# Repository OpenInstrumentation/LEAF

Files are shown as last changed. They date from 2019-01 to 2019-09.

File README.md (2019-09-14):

# LEAF
Logger for Environmental and Atmospheric Factors

CC-BY-SA 2019, A. Matheny, P. Marchetto, J. Powell, A. Rechner, J-y. Chuah, and S. Pierce

BoM: https://docs.google.com/spreadsheets/d/e/2PACX-1vQ8v-ukr38iTDn-cAedqp6OXnIay0lwoVsFbz_EMlWamA66PgREalaegVoSEzRlPvawVt73zznOhLpU/pubhtml or any of the BoM files above.

# Purpose
The LEAF is designed to be a modular sensing system, capable of measuring meteorological, hydrological, and other environmental parameters. In the design detailed in this repository, it was used to measure canopy throughfall of rain, soil moisture, and microclimate meteorological parameters, along with branch movement in the same tree the throughfall measurements were being made in.

# Files
The files in this repository are what's needed to program the different nodes of the sensing system network. The ground .ino file is different from the branches because it measures soil moisture as well; both of the .ino files are designed to be uploaded via Particle's online IDE at http://build.particle.io/. The catalog file includes all of the different items as priced at the time of the build, and the BoM includes direct links to them. The deployment file shows roughly what the initial instance looked like in its first deployment. The .brd and .sch files are Eagle board and schematic files, respectively, used to make PCBs for the system.

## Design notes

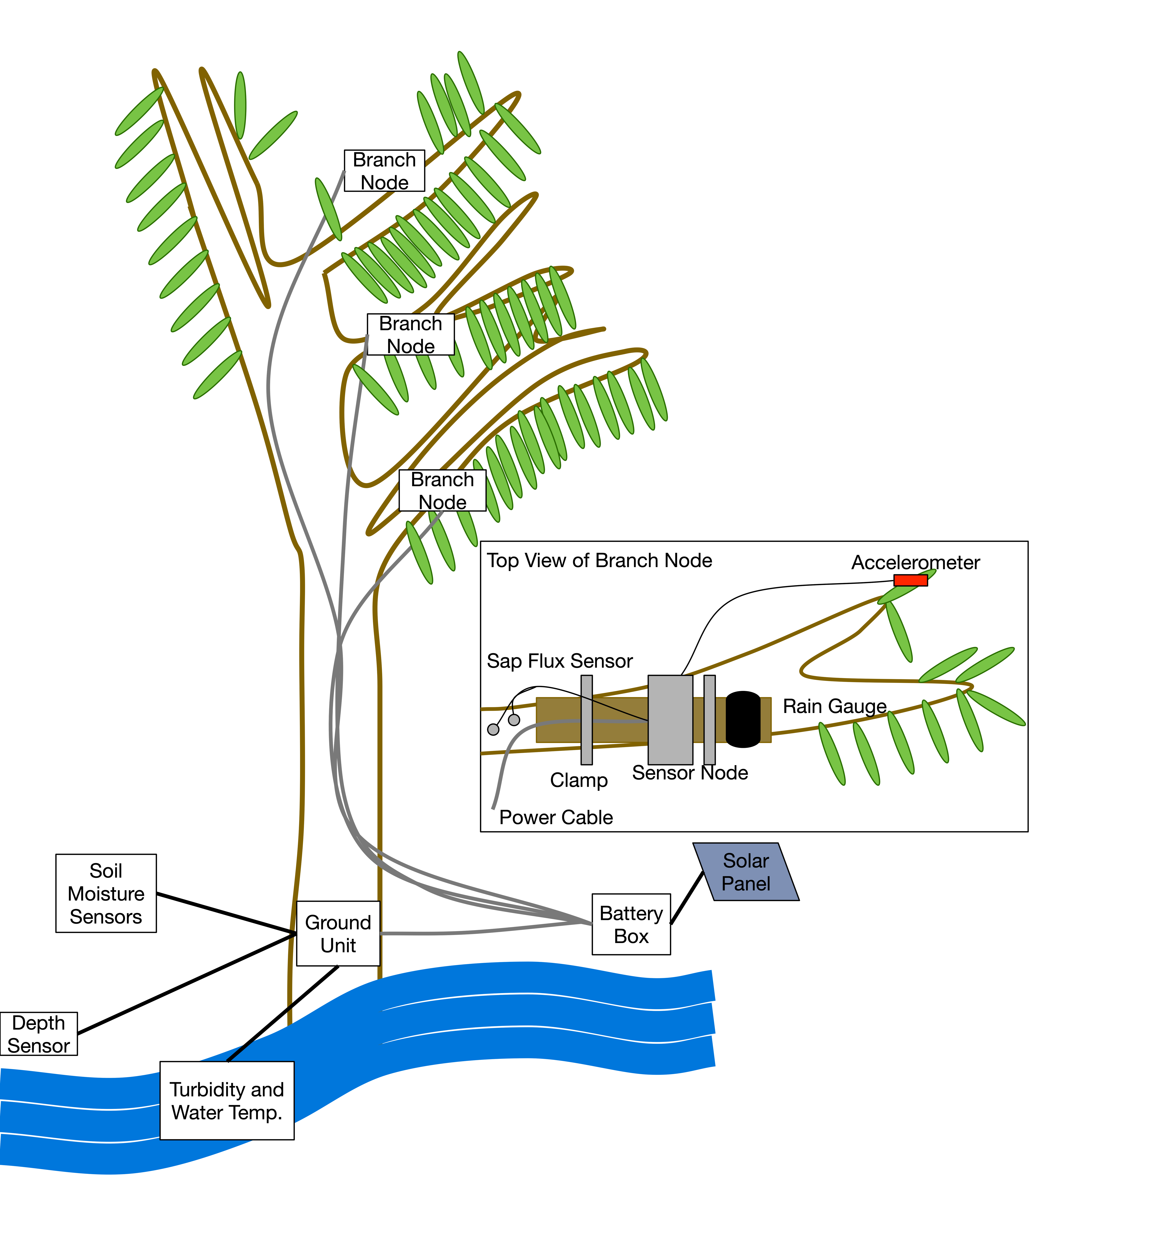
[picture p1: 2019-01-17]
LEAF Deployment.png

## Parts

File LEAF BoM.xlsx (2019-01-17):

Item | Qty | System | URL | Price Per | Extended Price | Material
Accelerometer/9DoF | 3 | Branch Node | https://www.amazon.com/SparkFun-13944-9DoF-Sensor-Stick/dp/B01LBLPN44 | $25 | $75 | Semiconductor
Enclosure | 4 | Branch/Ground Node | https://www.amazon.com/dp/B07CWFTJ9Z/ref=sspa_dk_detail_2?psc=1&pd_rd_i=B07CWFTJ9Z | $15 | $60 | Polymer
Flathead Screws, 1/4-20 SS | 1 | Branch/Ground Node | https://www.amazon.com/Machine-Screws-Phillips-Stainless-Quantity/dp/B01LYTB24M?s=industrial | $9 | $9 | Metal
T-Nuts, 1/4-20 SS | 1 | Branch/Ground Node | https://www.amazon.com/Stainless-Threaded-Quantity-Bolt-Dropper/dp/B01LFFB4BW?s=industrial | $16 | $16 | Metal
Buck Regulator | 1 | Branch/Ground Node | https://www.amazon.com/DZS-Elec-Adjustable-Electronic-Stabilizer/dp/B06XRXYHCB?s=industrial | $14 | $14 | Semiconductor
18/4 Cable | 1 | Branch/Ground Node | https://www.amazon.com/gp/offer-listing/B00KXYZT0O?condition=all | $200 | $200 | Metal
Thermocouple Amp/ADC | 4 | Branch/Ground Node | https://www.amazon.com/Adafruit-Universal-Thermocouple-Amplifier-MAX31856/dp/B01LZBBI7D?s=industrial | $19 | $76 | Semiconductor
Conformal Coating | 1 | Branch/Ground Node | https://www.amazon.com/MG-Chemicals-Silicone-Modified-Conformal/dp/B07BSK5S7B | $13 | $13 | Polymer
DHT22 T/RH | 1 | Branch/Ground Node | https://www.amazon.com/AM2302-Digital-Temperature-Humidity-Sensor/dp/B0748DBJR5 | $26 | $26 | Semiconductor
Protoboard | 1 | Branch/Ground Node | https://www.amazon.com/Double-Sided-Board-Prototype-Paxcoo/dp/B01N3161JP | $11 | $11 | Composite
Particle Electron | 4 | Branch/Ground Node | https://www.amazon.com/Particle-Electron-Internet-Development-Electronics/dp/B01BUGMNES | $70 | $280 | Semiconductor
Cable Gland | 1 | Branch/Ground Node | https://www.amazon.com/Plastic-Waterproof-Adjustable-Glands-Protectors/dp/B07GJDYGP5 | $10 | $10 | Polymer
Relay | 1 | Branch/Ground Node | https://www.amazon.com/Electronics-Salon-SPST-NO-Power-Relay-Module/dp/B079FQMCZ1 | $15 | $15 | Composite
0.1" Headers | 1 | Branch/Ground Node | https://www.amazon.com/SamIdea-Connector-Headers-Arduino-Prototype/dp/B07JN1KP7W | $9 | $9 | Composite
Shrink Tube | 1 | Branch/Ground Node | https://www.amazon.com/270-pcs-Adhesive-Assortment-MILAPEAK/dp/B0771K1Z7Q | $12 | $12 | Polymer
OpenLog | 4 | Branch/Ground Node | https://www.amazon.com/Openlog-Serial-Recorder-ATmega328-Support/dp/B07KM5BZR4 | $6 | $24 | Semiconductor
µSD Cards | 1 | Branch/Ground Node | https://www.amazon.com/PACK-SanDisk-MicroSD-SDSDQAB-008G-Packaging/dp/B00MHZ6ZJQ?s=pc | $22 | $22 | Semiconductor
0.1" Screw Terminals | 2 | Branch/Ground Node | https://www.amazon.com/Simpo-2-54mm-Terminal-150V6A-Material/dp/B07DG4798T | $8 | $16 | Composite
Resistor Assortment | 1 | Ground Node | https://www.amazon.com/Resistor-Assortment-Kit-Thermistor-Photoresistor/dp/B0792M83JH?s=industrial | $8 | $8 | Composite
Color Sensor | 1 | Ground Node | https://www.amazon.com/WINGONEER-TCS3200-Detector-Recognition-Arduino/dp/B06XHL79SQ | $10 | $10 | Semiconductor
Clear Epoxy | 1 | Ground Node | https://www.amazon.com/Clear-Casting-Coating-Epoxy-Resin/dp/B07BM9LHRB | $25 | $25 | Polymer
Ultrasonic Distance Sensor | 1 | Ground Node | https://www.amazon.com/SainSmart-HC-SR04-Ranging-Detector-Distance/dp/B004U8TOE6?s=electronics | $8 | $8 | Semiconductor
Solar Panel | 1 | Power | https://www.amazon.com/HQST-Watt-Polycrystalline-Solar-Panel/dp/B018BOK9WU?s=lawn-garden | $95 | $95 | Semiconductor
Solar Panel Connectors | 1 | Power | https://www.amazon.com/Connector-Extension-Connect-Branch-Parallel/dp/B07FYFMCZV?s=lawn-garden | $14 | $14 | Metal
Battery Box | 1 | Power | https://www.amazon.com/Plano-Tactical-Custom-Ammo-Box/dp/B0747JPRW4 | $6 | $6 | Polymer
Terminal Strips | 1 | Power | https://www.amazon.com/Positions-Terminal-Pre-Insulated-Barrier-MILAPEAK/dp/B07CLY5N9T | $13 | $13 | Metal
Charge Controller | 1 | Power | https://www.amazon.com/dp/B010FNO9NU | $10 | $10 | Semiconductor
Battery, 12 V SLA | 1 | Power | https://www.amazon.com/ExpertPower-EXP1290-Volt-Rechargeable-battery/dp/B00A82A3QG | $28 | $28 | Composite
Spade Connector, F | 1 | Power | https://www.amazon.com/Glarks-Disconnect-Electrical-Connectors-Assortment/dp/B01EE4B1KU | $7 | $7 | Metal
Fork Connector Assortment | 1 | Power | https://www.amazon.com/Cofufu-Insulated-Connector-Electrical-Terminal/dp/B07KRK8GQG | $13 | $13 | Metal
Staples | 1 | Power | https://www.amazon.com/Gardner-Bender-MSI-200JT-Insulated-Secures/dp/B00PSFPW1O?s=industrial | $6 | $6 | Metal
Armored Cable, 14/2 MC | 1 | Power | https://www.amazon.com/Southwire-68579201-Armorlite-Aluminum-Armored/dp/B000IKK44E | $100 | $100 | Metal
Total |  |  |  |  | $1231

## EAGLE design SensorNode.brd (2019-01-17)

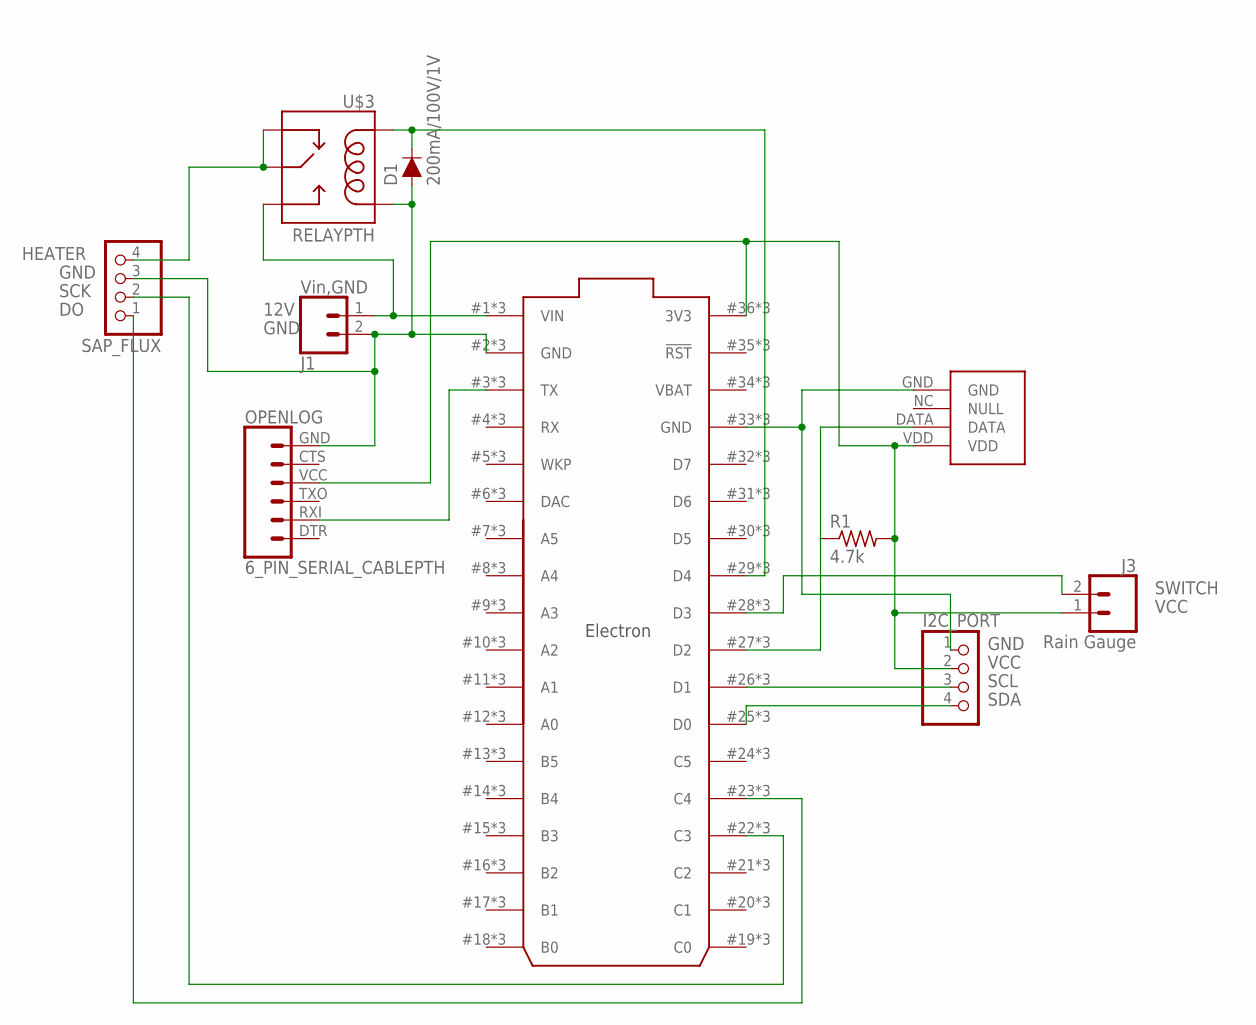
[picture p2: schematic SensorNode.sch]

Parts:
D1: 200mA/100V/1V; DIODE-1N4148
I2C_PORT: PINHD-1X4; 1X04
J1: Vin,GND; SCREWTERMINAL-3.5MM-2
J3: Rain Gauge; SCREWTERMINAL-3.5MM-2
OPENLOG: 6_PIN_SERIAL_CABLEPTH; FTDI_BASIC
R1: 4.7k; 0204/7
SAP_FLUX: PINHD-1X4; 1X04
U$1: ELECTRON_WITH_STACKABLE_HEADERS; ELECTRON_STACKABLE
U$2: DHT22
U$3: RELAYPTH; RELAY-G5Q

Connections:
12V: J1.1, U$1.1 (VIN), U$1.#1 (VIN), U$1.@1 (VIN), U$3.3 (NO)
DO: SAP_FLUX.1, U$1.23 (C4), U$1.#23 (C4), U$1.@23 (C4)
GND: D1.A, I2C_PORT.1, J1.2, OPENLOG.GND (6), SAP_FLUX.3, U$1.2 (GND), U$1.33 (GND), U$1.#2 (GND), U$1.#33 (GND), U$1.@2 (GND), U$1.@33 (GND), U$2.GND, U$3.1 (COIL2)
HEATER: SAP_FLUX.4, U$3.2 (MAIN), U$3.4 (NC)
unnamed: OPENLOG.RXI (2), U$1.3 (TX), U$1.#3 (TX), U$1.@3 (TX)
unnamed: U$1.27 (D2), U$1.#27 (D2), U$1.@27 (D2), U$2.DATA
unnamed: D1.C, U$1.29 (D4), U$1.#29 (D4), U$1.@29 (D4), U$3.5 (COIL1)
SCK: SAP_FLUX.2, U$1.22 (C3), U$1.#22 (C3), U$1.@22 (C3)
SCL: I2C_PORT.3, U$1.26 (D1), U$1.#26 (D1), U$1.@26 (D1)
SDA: I2C_PORT.4, U$1.25 (D0), U$1.#25 (D0), U$1.@25 (D0)
SWITCH: J3.2, U$1.28 (D3), U$1.#28 (D3), U$1.@28 (D3)
VBAT: U$1.34 (VBAT), U$1.#34 (VBAT), U$1.@34 (VBAT)
VCC: I2C_PORT.2, J3.1, OPENLOG.VCC (4), R1.2, U$1.36 (3V3), U$1.#36 (3V3), U$1.@36 (3V3), U$2.VDD

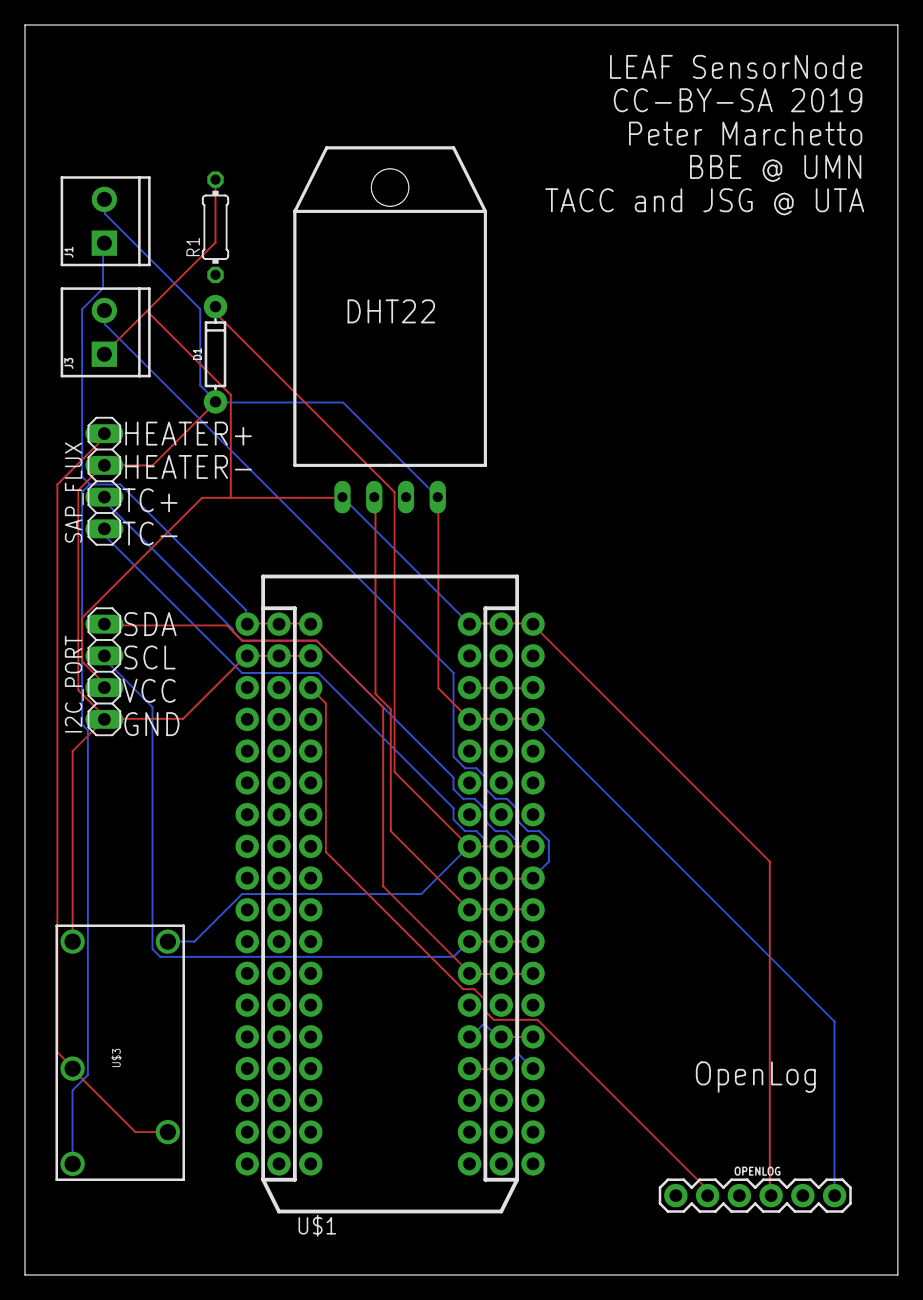
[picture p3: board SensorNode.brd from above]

Board: 2 copper layers, 69.8 x 100.0 mm, 10 parts (0 on the bottom side), 13 nets.

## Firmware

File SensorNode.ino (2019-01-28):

// This #include statement was automatically added by the Particle IDE.
//#include <Adafruit_BME280.h>




/* 
 Yggdrasil Code
 
 Particle Electron Pin Outs for Sensors
 
 Sap Flux DIFF   - WKP    A7 (WKP)

 SD Card        - MOSI   A5 <-- Todo
 SD Card        - MISO   A4
 SD Card        - SCK    A3
 SD Card        - SS(CS) A2
 Temp           - D-In   A1
 Pressure       - A-In   B0
 Soil-1         - A-In   B5
 Soil-2         - A-In   B4
 
 Ultra Sonic    - Echo   D7 <-- Relay for Batt kick (Test)
 Ultra Sonic    - Trigg  D6
 DHT22          - D-In   D5
 Rain Bucket    - A-In   D4 <-- Interrupt  
 Water Detector - A-In   D3 <-- Interrupt
 Accel.         - SCL    D1 <--|
 Accel.         - SDA    D0    |---Share SCL and SDA I2C
 BME280         - SCL    D1    |
 BME280         - SDA    D0 <--|
 Turbidity      - D-In   C4 <-- Todo
 Turbidity      - S3     C3 
 Turbidity      - S2     C2
 Turbidity      - S1     C1
 Turbidity      - S0     C0
 */
 
// Included Libraries
// Additional Math Functions
#include <math.h>
// DHT22 for Temp, Humidity and Pressure
#include <Adafruit_DHT_Particle.h>
// SDCard Reader/Writer
#include <SdFat.h>
// Ultra Sonic HC-SR04
#include <HC-SR04.h>
// Accelerometer (I2C-0x6A) 9DOF 
#include <SparkFunLSM9DS1.h>
// Temp /Relative humidity and Pressure (I2C- 0x77 or 0x76?) BME280
#include <SparkFunBME280.h>
// Water Digital Temp DS18B20
#include <DS18B20.h>

//------------------------------------------------------------------------------
// Sap Flux Hot Definition
#define Sap_Flux_Hot A7


//------------------------------------------------------------------------------
// Sap Flux Cold Definition
#define Sap_Flux_Cold A6


//------------------------------------------------------------------------------
// SDCard Definition
#define SPI_CONFIGURATION 0
// Setup SPI configuration.
// Primary SPI with DMA
// SCK => A3, MISO => A4, MOSI => A5, SS => A2 (default)
SdFat sd;
File myFile;
const uint8_t chipSelect = SS; // Default SD chip select is SS pin
// store error strings in flash to save RAM
#define error(s) sd.errorHalt(F(s))

//------------------------------------------------------------------------------
// Digital Temp DS18B20
#define DS18B20PIN A1
DS18B20  ds18b20(DS18B20PIN, true);


//------------------------------------------------------------------------------
// Pressure Definition
#define WATER_PRESSURE A0


//------------------------------------------------------------------------------
// Soil Moisture 1 Definition
#define Soil_Moisture_1 B5


//------------------------------------------------------------------------------
// Soil Moisture 2 Definition
#define Soil_Moisture_2 B4


//------------------------------------------------------------------------------
// Depth Sensor HC-SR04 Pin Definition
//const int echoPin = D7;
//const int triggerPin = D6;
//HC_SR04 waterlevel = HC_SR04(triggerPin, echoPin);


//Battery Relay
#define batt_relay D7


//------------------------------------------------------------------------------
//DHT22 Definition
#define DHTPIN D5     // Ref above pins
#define DHTTYPE DHT22		// DHT 22 (AM2302)
// Connect pin 1 (on the left) of the sensor to +5V
// Connect pin 2 of the sensor D5
// Connect pin 4 (on the right) of the sensor to GROUND
// Connect a 10K resistor from pin 5 (data) to pin 1 (power) of the sensor
DHT dht(DHTPIN, DHTTYPE);


//------------------------------------------------------------------------------
// RAIN DRIP BUCKET DEFINITION
#define DRIP_SENSOR_PIN D4

//------------------------------------------------------------------------------
// INTERNAL WATER SENSOR DEFINITION
#define WATER_SENSOR_PIN D3


//------------------------------------------------------------------------------
//Accelerometer 9DOF I2C Definition
LSM9DS1 imu;

// SDO_XM and SDO_G are both pulled high, so our addresses are:
#define LSM9DS1_M	0x1E // Would be 0x1C if SDO_M is LOW
#define LSM9DS1_AG	0x6B // Would be 0x6A if SDO_AG is LOW

////////////////////////////
// Sketch Output Settings //
////////////////////////////
#define PRINT_CALCULATED
//#define PRINT_RAW
#define PRINT_SPEED 250 // 250 ms between prints

// Earth's magnetic field varies by location. Add or subtract 
// a declination to get a more accurate heading. Calculate 
// your's here:
// http://www.ngdc.noaa.gov/geomag-web/#declination
#define DECLINATION 3.44 // Declination (degrees) in Austin, TX.


//------------------------------------------------------------------------------
// T/RH/P BME280 I2C Definition
BME280 t_rh_p_bme;
//Adafruit_BME280 t_rh_p_bme;
//------------------------------------------------------------------------------
// TURBIDITY SENSOR DEFINITION
#define TURBIDITY_INPUT_PIN C4
#define TURBIDITY_S3_PIN C3
#define TURBIDITY_S2_PIN C2
#define TURBIDITY_S1_PIN C1
#define TURBIDITY_S0_PIN C0

#define SEALEVELPRESSURE_HPA (1013.25)

//-----------------------------------------------------------------------------
//  GLOBAL VARIABLE DECLARATIONS FOR PARTICLE CALL VARIABLE USAGE
double sf_h, sf_c, h_dht, t_dht, t_bme, rel_humid_bme, p_bme, ax, ay, az;
int accel_test = 1;
double slam=0.;
String myID = System.deviceID();
bool dht_status = true;

//-----------------------------------------------------------------------------
//  GLOBAL INTERRUPT VARIABLES AND HANDLER FOR RAINBUCKET

 volatile bool bucket_state = false;
 const unsigned int DEBOUNCE_TIME = 750;
 static unsigned long last_interrupt_time = 0;
 
 int rain = -1;


//long int loopCount = 0; //If a set number of loops are to happen before microcontroller sleep
unsigned long lastTime = 0;

const String key = "CZJ4L4MWV7ZE3HDS";

//----------------------------------------------------//
//            BEGIN SETUP                             //
//----------------------------------------------------//

void setup() {
  Serial.begin(9600);
  Particle.publish("ImOn", "Entering Setup");
  
  
    // PRESENT VARIABLES FOR TESTING
    /*Particle.variable("Sap Flux Ht", sf_h);
    Particle.variable("DHT Temp C", t_dht);
    Particle.variable("BME Temp", t_bme);
    Particle.variable("Lp Run Count", loopCount);
    */
    //Serial.println(myID);
    //Particle.variable("Device ID", myID);
    
    Particle.function("KickBatt", kickbatt);
    
    
    


// Initialize sd card  
  // Initialize SdFat or print a detailed error message and halt
  // Use half speed like the native library.
  Particle.publish("SDCard_Setup", "Initializing");
  if (!sd.begin(chipSelect, SPI_HALF_SPEED)) {
    sd.initErrorHalt();
     Particle.publish("SDCard_Setup", "SD Card init failed");
    }


  // open the file for write at end like the "Native SD library"
  if (!myFile.open("startup.txt", O_RDWR | O_CREAT | O_AT_END)) {
    sd.errorHalt("opening startup.log for write failed");
    Particle.publish("SDCard_Setup", "SD Card startup.txt init failed");
  }

  // if the file opened okay, write to it:
 Time.zone(-6);
 time_t time = Time.now();
 String timeStamp = Time.format(time, TIME_FORMAT_ISO8601_FULL);
  
  
  
  
  myFile.println("////////////////SD Card initialized///////////////////");
  myFile.printf(timeStamp,"\n");
  myFile.printf("fileSize: %d\n", myFile.fileSize());
  myFile.printf("Device ID ",myID.c_str(),"\n");
  myFile.printf("[--------------------------------------------------]\n");
  
  // close the file:
  myFile.close();
  //Serial.println("done.");


/*
  // re-open the file for reading:
  if (!myFile.open("test.txt", O_READ)) {
    sd.errorHalt("opening test.txt for read failed");
  }
  Serial.println("test.txt content:");

  // read from the file until there's nothing else in it:
  int data;
  while ((data = myFile.read()) >= 0) {
    Serial.write(data);
  }
  // close the file:
  myFile.close();

*/


//------------------------------------------------------------------------------
//Initialize HC-SR04 Waterlevel
//waterlevel.init();
delay (1000);

//------------------------------------------------------------------------------
//Initialize DHT22

Particle.publish("DHT_Setup", "DHT Initializing");
dht.begin();
delay(1000);
    Particle.publish("DHT_Test", String(dht.getTempCelcius()));




/*
//------------------------------------------------------------------------------
//Initialize Accelerometer 9DOF I2C
imu.settings.device.commInterface = IMU_MODE_I2C;
imu.settings.device.mAddress = LSM9DS1_M;
imu.settings.device.agAddress = LSM9DS1_AG;
  // The above lines will only take effect AFTER calling
  // imu.begin(), which verifies communication with the IMU
  // and turns it on.
  if (!imu.begin()) {
      Particle.publish("IMU_Setup", "Accelerometer Failed");
      accel_test = 0;
   }

*/

//------------------------------------------------------------------------------
//Initialize BME280
//I2C Setup
 Particle.publish("BME_Setup", "Initializing");

//t_rh_p_bme.settings.commInterface = I2C_MODE;
//t_rh_p_bme.settings.I2CAddress = 0x76; //Could be 0x76


	t_rh_p_bme.settings.commInterface = I2C_MODE;
	t_rh_p_bme.settings.I2CAddress = 0x76;

	//For SPI enable the following and dissable the I2C section
	//t_rh_p_bme.settings.commInterface = SPI_MODE;
	//t_rh_p_bme.settings.chipSelectPin = 10;


	//***Operation settings*****************************//

	//runMode can be:
	//  0, Sleep mode
	//  1 or 2, Forced mode
	//  3, Normal mode
	t_rh_p_bme.settings.runMode = 3; //Normal mode

	//tStandby can be:
	//  0, 0.5ms
	//  1, 62.5ms
	//  2, 125ms
	//  3, 250ms
	//  4, 500ms
	//  5, 1000ms
	//  6, 10ms
	//  7, 20ms
	t_rh_p_bme.settings.tStandby = 0;

	//filter can be off or number of FIR coefficients to use:
	//  0, filter off
	//  1, coefficients = 2
	//  2, coefficients = 4
	//  3, coefficients = 8
	//  4, coefficients = 16
	t_rh_p_bme.settings.filter = 4;

	//tempOverSample can be:
	//  0, skipped
	//  1 through 5, oversampling *1, *2, *4, *8, *16 respectively
	t_rh_p_bme.settings.tempOverSample = 5;

	//pressOverSample can be:
	//  0, skipped
	//  1 through 5, oversampling *1, *2, *4, *8, *16 respectively
    t_rh_p_bme.settings.pressOverSample = 5;

	//humidOverSample can be:
	//  0, skipped
	//  1 through 5, oversampling *1, *2, *4, *8, *16 respectively
	t_rh_p_bme.settings.humidOverSample = 5;

	
	Serial.print("Program Started\n");
	Serial.print("Starting BME280... result of .begin(): 0x");

	//Calling .begin() causes the settings to be loaded
	delay(10);  //Make sure sensor had enough time to turn on. BME280 requires 2ms to start up.
	//Particle.publish("BME_Setup", "BME Failed");
	if (!t_rh_p_bme.begin()){
    Particle.publish("BME_Setup", "BME Failed");
}
	
	//Serial.println(t_rh_p_bme.begin(), HEX);

	Serial.print("Displaying ID, reset and ctrl regs\n");

	Serial.print("ID(0xD0): 0x");
	Serial.println(t_rh_p_bme.readRegister(BME280_CHIP_ID_REG), HEX);
	Serial.print("Reset register(0xE0): 0x");
	Serial.println(t_rh_p_bme.readRegister(BME280_RST_REG), HEX);
	Serial.print("ctrl_meas(0xF4): 0x");
	Serial.println(t_rh_p_bme.readRegister(BME280_CTRL_MEAS_REG), HEX);
	Serial.print("ctrl_hum(0xF2): 0x");
	Serial.println(t_rh_p_bme.readRegister(BME280_CTRL_HUMIDITY_REG), HEX);
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

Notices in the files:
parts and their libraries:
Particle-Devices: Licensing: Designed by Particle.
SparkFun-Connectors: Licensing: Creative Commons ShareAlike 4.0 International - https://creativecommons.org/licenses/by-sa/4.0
